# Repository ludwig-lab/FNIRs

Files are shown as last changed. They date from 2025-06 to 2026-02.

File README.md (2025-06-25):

# FNIRs
This project aims to create a FNIRs device that will connect directly to the TDT. The current circuit boards in this repository include as follows:
Detector: This board includes a photodiode sensor, and an amplifier.
Emitter: This board contains 3 different LED types, one is IR, one is red, and one is a bicolor LED with both IR and red light. This board is for testing to see which LED or LED combination we should use.
Port: This will plug into the TDT Subject Interface Module.

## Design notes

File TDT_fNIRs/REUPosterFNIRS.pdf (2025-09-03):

# A Functional Near-Infrared Spectroscopy (fNIRS) System for Monitoring Cerebral Blood Flow in Response to Cranial Nerve Stimulation

Hailey Haglid¹, Keith Kozma², Brandon Coventry²,3,4, James Trevathan²,3,4, Kip Ludwig²,3,4

1. Department of Biomedical Engineering, Purdue University 2. Department of Biomedical Engineering, University of Wisconsin Madison 3. Department of Neurological Surgery, University of Wisconsin Madison 4. Wisconsin Institute for Translational Neuroengineering

Supported by a generous gift from The University of Wisconsin-Madison Graduate School and grants from the National Science Foundation (DMR-1720415) and the Department of Energy (DE-EE0009285).

## Device Design

## Open-Source Files

## Device Fabrication

## Next Steps

## Project Goal

Background | Design Validation
Design Specification | Value
Voltage Output (Max) | 500 mV
Sampling Frequency | 20 kHz
Voltage Input (Max) | ± 2.5 V

Functional near-infrared
spectroscopy (fNIRS)
- Non-invasive
- Monitors hemodynamics
- Utilizes optical
absorption properties of
hemoglobin in the blood

Cranial Nerve Stimulation
- Cranial nerve stimulation causes changes to
cerebral blood flow

LEDs Detector

This project details the design of an fNIRS device that interfaces with an electrophysiological system, allowing for synchronized stimulation and hemodynamic recordings

Design specifications for the fNIRS were set based Tucker-Davison Technologies
(TDT) system requirements

Detector Design
- A photodiode emits current in response to light
- A Transimpedance Amplifier (TIA) converts that current to voltage
- TIA component values were calculated and simulated

TIA LTSpice Simulation

Emitter Design
- Hemoglobin absorbs light
- Deoxygenated <790nm
- Oxygenated >790nm
- LEDs of 730nm and 850nm

TDT Port Design
- Designed and labeled PCBs that fit over the TDT
connector pins

PCB Design
- PCBs were designed in
KiCAD
- Custom footprints
- Decoupling capacitors
were placed near power
sources
Emitter | Detector

TDT Port Connectors

Printed and Soldered Boards

FFT of LED through Skin

- Design an apparatus to hold the fNIRS against the skin
- Real time analysis of blood flow changes
- Improve user interface and documentation for the TDT

Accelerometer PCBs

## Second Iteration

Initial Iteration Issues
- The pins did not fit the connector perfectly
- Motion artifacts could be seen while testing
Verification Test | Result
Preliminary PCB Testing (Multimeter) | No unwanted shorts
Maximum voltage under bright light | <400 mV
LED Functionality testing with TDT | LEDs flash
FNIRs with against skin testing | Detector can read signals from the LEDs on the TDT
Accelerometer XYZ testing | XYZ acceleration can be seen on TDT

## Contact Information

## Acknowledgements

This work was made possible through the support of the UW– Madison SURE Program, Professor Kip Ludwig, all my lab mates. Thank you!

If you would like the design files or component information for this project, please visit our GitHub

Hailey “Lee” Haglid
Haglid@purdue.edu

Dr. Kip Ludwig
Kip.Ludwig@wisc.edu

Connect on
LinkedIn

Prototype on Perfboard

Motion Artifacts
- Movement can
create voltage
spikes unrelated to
hemodynamics
- Stimulating nerves
can cause off target
muscle activation
- Participants
naturally move while
sitting

Accelerometer
- An accelerometer
was added to the
design to capture
motion
- Acceleration in the
XYZ directions can
be measured and
quantified

TDT Raw Outputs while Generating Motion Artifacts Visualized

x

y

z

fNIRS

Assembled fNIRS

Detector

Emitter

TDT Interface

Detector Signals

LED Controls

Subject Interface
Module

fNIRS Device

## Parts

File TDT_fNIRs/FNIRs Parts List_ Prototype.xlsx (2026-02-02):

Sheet: Sheet1
Part | Specs | Price | Qt | Total Price | Link
LED IR/RED | 850nm, 660nm | $0.54 | 32 | $17.18 | https://www.digikey.com/en/products/detail/american-opto-plus-led/L955SRIRC-TR/13243448
Photodiode |  | $1.24 | 8 | $9.92 | https://www.digikey.com/en/products/detail/vishay-semiconductor-opto-division/VEMD5060X01/5879084
Opamp | low voltage | $0.20 | 20 | $4.00 | https://www.digikey.com/en/products/detail/microchip-technology/MCP6006UT-E-OT/13985884
Resistors |  | $12.50 | 1 | $12.50 | https://www.digikey.com/en/products/detail/lumimax-optoelectronic-technology/CR1206FK-60/25628291
Caps |  | $16.00 | 2 | $32.00 | https://www.digikey.com/en/products/detail/lumimax-optoelectronic-technology/AECSMDK-11/21710722
LED IR | 850nm | $0.26 | 10 | $2.60 | https://www.digikey.com/en/products/detail/inolux/IN-P32ZTIR/10384796
LED RED | 730nm | $0.49 | 10 | $4.91 | https://www.digikey.com/en/products/detail/lumileds/L1SP-FRD0002800000/9805569
Total |  |  |  | $83.11

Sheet: Justification
Needed Parameters
Wave length | 850nm, 660nm | https://www.pluxbiosignals.com/products/fnirs-pioneer

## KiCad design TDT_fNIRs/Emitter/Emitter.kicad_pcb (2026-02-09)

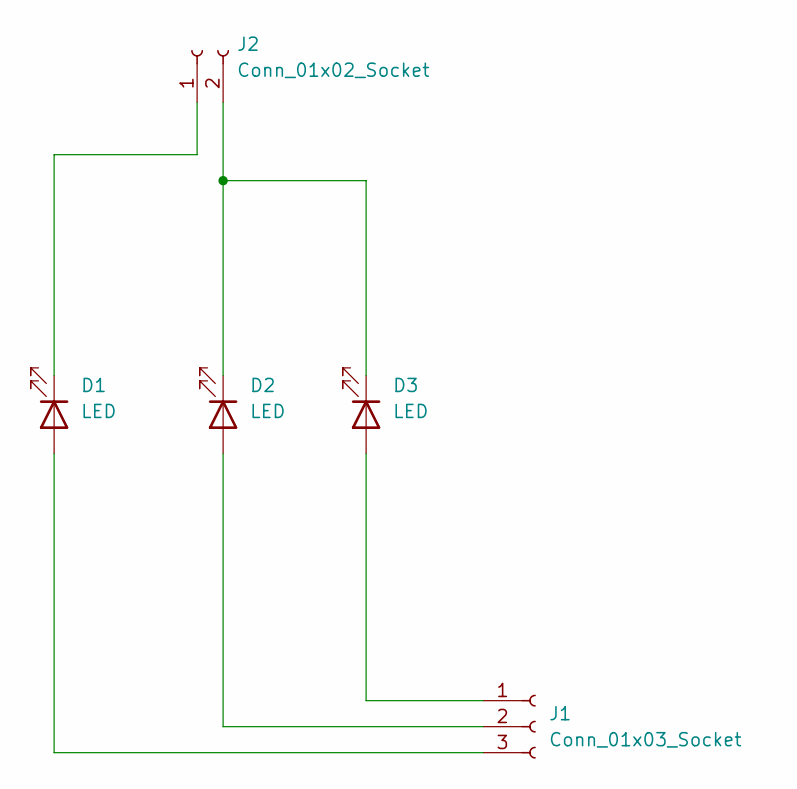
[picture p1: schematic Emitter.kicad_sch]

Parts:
D1: LED; BiColorLED
D2: LED; LEDIR
D3: LED; LEDR
J1: Conn_01x03_Socket; PinSocket_1x03_P2.54mm_Vertical
J2: Conn_01x02_Socket; PinSocket_1x02_P2.54mm_Vertical

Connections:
unnamed: D1.2 (A), J1.3
unnamed: D1.1 (K), J2.1
unnamed: D2.2 (A), J1.2
unnamed: D2.1 (K), D3.1 (A), J2.2
unnamed: D3.2 (K), J1.1

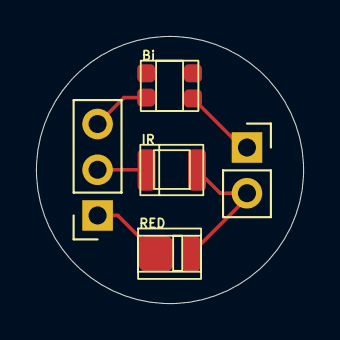
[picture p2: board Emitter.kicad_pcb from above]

Board: 2 copper layers, 14.8 x 14.8 mm, 5 parts (0 on the bottom side), 5 nets.

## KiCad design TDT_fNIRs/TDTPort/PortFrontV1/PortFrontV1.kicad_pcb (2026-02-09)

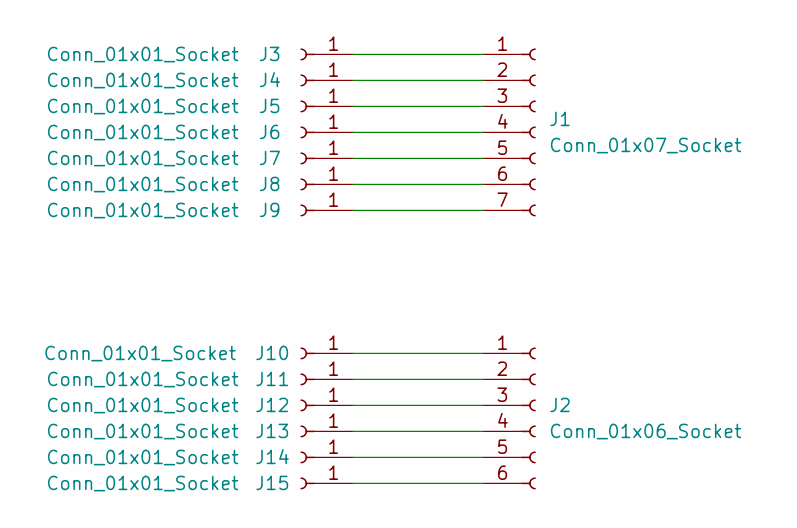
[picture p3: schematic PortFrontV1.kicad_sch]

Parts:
J1: Conn_01x07_Socket; PinSocket_1x07_P2.54mm_Vertical
J2: Conn_01x06_Socket; PinSocket_1x06_P2.54mm_Vertical
J3, J4, J5, J6, J7, J8, J9, J10, J11, J12, J13, J14, J15: Conn_01x01_Socket; PinHeader_1x01_P1.00mm_Vertical

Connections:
unnamed: J1.1, J3.1
unnamed: J1.2, J4.1
unnamed: J1.3, J5.1
unnamed: J1.4, J6.1
unnamed: J1.5, J7.1
unnamed: J1.6, J8.1
unnamed: J1.7, J9.1
unnamed: J2.1, J10.1
unnamed: J2.2, J11.1
unnamed: J2.3, J12.1
unnamed: J2.4, J13.1
unnamed: J2.5, J14.1
unnamed: J2.6, J15.1

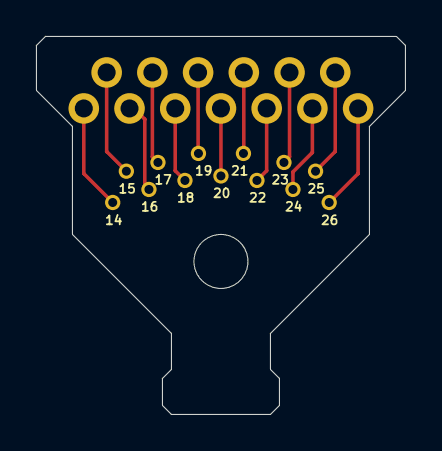
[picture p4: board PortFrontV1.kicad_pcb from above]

Board: 2 copper layers, 20.5 x 21.0 mm, 15 parts (0 on the bottom side), 13 nets.

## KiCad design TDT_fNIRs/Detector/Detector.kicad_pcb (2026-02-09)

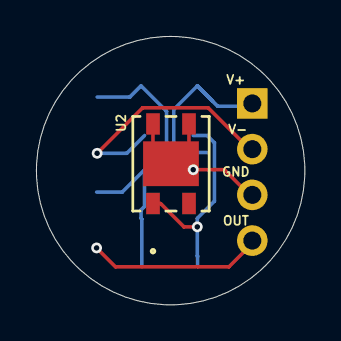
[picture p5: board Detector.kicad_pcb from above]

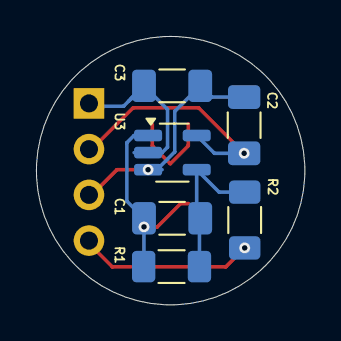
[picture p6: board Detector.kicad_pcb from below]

Board: 2 copper layers, 14.9 x 14.9 mm, 8 parts (6 on the bottom side), 6 nets.

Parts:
C1, C2, C3: C; C_1206_3216Metric_Pad1.33x1.80mm_HandSolder
R1, R2: R_US; R_1206_3216Metric_Pad1.30x1.75mm_HandSolder
U2: VEMD5060X01; SMD_VEMD5-5X4_VIS
U3: OPA376xxDCK; SOT-23-5_HandSoldering
V+: Conn_01x04_Socket; PinSocket_1x04_P2.54mm_Vertical

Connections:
unnamed: C1.2, R1.2, R2.1, U3.4
unnamed: C1.1, R1.1, U2.1 (ANODE), U3.1 (+)
Vneg: C2.1, U3.5 (V+), V+.2
Vpos: C3.1, U3.2 (V-), V+.1
gnd: C2.2, C3.2, U2.3 (CATHODE), U2.4 (CATHODE), U2.5 (CATHODE), U3.3 (-), V+.3
output: R2.2, V+.4

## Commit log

2026-02-09 Restructure project folder to include fNIRs analysis
    [Detector-NPTH-drl_map.gbr, Detector-PTH-drl_map.gbr, Detector.kicad_pcb, Detector.kicad_sch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]
2026-02-09 Added flexNIRs functions and test scripts
    [Detector-NPTH-drl_map.gbr, Detector-PTH-drl_map.gbr, Detector.kicad_pcb, Detector.kicad_sch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]
